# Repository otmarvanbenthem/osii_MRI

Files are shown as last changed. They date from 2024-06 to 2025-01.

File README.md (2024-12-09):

# OSII Mini 

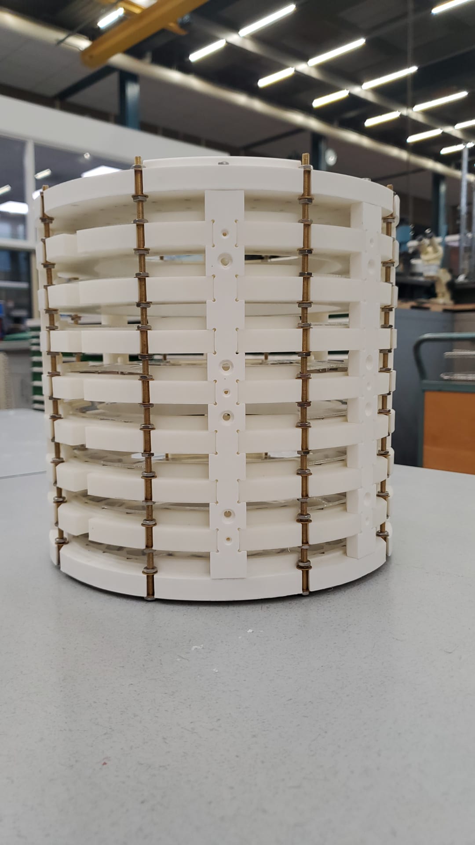
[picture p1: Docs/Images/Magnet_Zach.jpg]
Zach_magnet


Documentation for building the open source ultra low-field MRI for education

Magnetic Resonance Imaging (MRI) is one of the most powerful and versatile non-invasive medical imaging devices. 
Ultra low-field MRI scanners such as __OSII One__ have recently reached the maturity level of [attempting eligibility for standardization and medical certification](https://www.opensourceimaging.org/). 
These open source projects has pooled the knowledge and experience of many experts and can be built and maintained for a fraction of the price of current instruments. 

This educational project is a collaboration initiated by the [Lili's Proto Lab](https://www.uu.nl/lpl) with the aim of preparing a hands-on workshop for student teams to replicated an OSII-inspired functioning MRI.
Student teams can be a great force in progressing this field. 
Collectively, they can enhance the accuracy and utility of open-source MRI devices through rigorous calibration procedures, iterative testing, and collaboration with experts in both engineering and medical fields.  

## Getting started

These are the essential elements for creating a magnetic resonance image:
+ A uniform magenetic field B0
+ Coils for creating field gradients in x, y, and z -directions
+ Coils for sending and recieving pulses
+ Electronics for creating the imaging pulse sequences
+ Software to control the sequences and reconstructing the images

In this repository, we have split the steps into independent experiments so that one can start building each of the elements and persome some benchmark measurements.

## Building the main magnet
To create a uniform base field, we use the [Halbach Array](https://en.wikipedia.org/wiki/Halbach_array) construction. Check these [build instructions](./Docs/FrameAssembly) and [design files](./Build/HalbachFrame).

The current design is adopted from the OSII mini magnet designed by Dr. Joshua Harper from [Sustainable MRI Lab](smrilab.com) and Thomas O'Reilly and [Andrew Webb at Leiden University](https://www.universiteitleiden.nl/en/staffmembers/andrew-webb#tab-2). The main change in our design is using lids for keeping small magnets in place instead glueing them.  

__The Halbach Frame:__
	+ 120 mm inner diameter 
	+ DSV 100 x100 x100 mm
	+ 396 magnets 12x12x12 mm
	+ 50 mT
	+ around 1200 Euros for a completed magnet
	
### Verifying the field uniformity
To achieve MR imaging, the base magnetic field must be uniform. Based on experience, the maximum allowed field inhomgeneity is 3000 ppm. The field uniformity can be checked with a 3D scanner. [See instructions](./Docs/Fieldscanner) forconverting a 3D printer into such a scanner.

### Shimming the main magnet
The uncorrected fluctuations in Halbach with only big 6x6x6 mm magnets can be as high as 15000 ppm. This uniformity must be improved by adding extra magnets in a process called [shimming](./Docs/Shimming). 
Because of this process, each Halbach assembly is unique.

### Gradient coils
To create a three dimensional MRI, the spatial information must be [encoded in time, frequency and phase response](https://mriquestions.com/how-to-locate-signals.html#/) along these orthogonal axes. This encodig requires controlling applying various field gradients, dynamically. This encoding is done with 3 gradient coils. Check these [build instructions](./Build/GradientCoils).

### Send and recieve circuitry
MRI is based on measuring quantum effect called the spin echo. In short, the water molecules can be excited in a way that they emit a a measurable radio frequency signal at a specific delay after their excitation. The excitation pulse can be much stronger than the echo pulse, and therfore delicate circuitry is necessary to separate the spin echo from other possible spurious signals. Check these [design consideration](./Docs/RFCoils)

### The MRI console
In MRI literature, all the electronic boards that are used for generating and analyzing the required RF sequences are collectively called the MRI console. Once a uniform B0 is constructed and proper RF coils are embedded in the assembly frame, in principle the setup can be combined with suitable commercial or open source consoles. Here is a list of consoles that have been tested with various low-field MRI devices.

+ [Kea2](https://magritek.com/products/kea/) provided by magritek
+ [OCRA](https://openmri.github.io/ocra/) built on top of [STEMlab/Red Pitaya](https://www.redpitaya.com/f130/STEMlab-board)

## Latest news

The build instructions for the gluefree Halbach magnet are posted in the [Build](./Build/HalbachFrame) folder.

## Outcomes

Our main goal to support the student teams who collaborate in replicating this low field MRI. 
In parallel, all outputs of this collaboration will be shared with the sister MRI project such as the OSII ONE. 

## Team

+ Utrecht University, Lilis Proto Lab:
	+ Project lead: Sanli Faez
	+ Contributors: Zachary Meredith, Low Field Legends (Experiment Design class of 2024)

+ Universidad Paraguayo Alemana: 
	+ Project lead: Joshua Harper
	+ Contributors: 

+ NIST Boulder: 
	+ Project lead: Stephen Ogier
	+ Contributors: Katy Keenan

+ New York University, Interactive Telecommunications Program:
	+ Greg Shakar
	
## MRI Resources
More information about MRIs and their operations can be found below:
+ [MRI Questions website maintained by Allen D. Elster](https://mriquestions.com/index.html)
+ [OSI<sup>2</sup> Repository:](https://gitlab.com/osii) Here you can find additional information about the original OSI<sup>2</sup> ONE

### Related projects
Several groups worldwide have succeeded in replicating this device or have created similar designs. 

+ [OSI2 ONE MR Scanner](https://www.opensourceimaging.org/project/osii-one/)
+ [OCRA Console](https://openmri.github.io/ocra/)
+ [Earth-field NMR](https://phas.ubc.ca/~michal/Earthsfield/) 
+ [Hallbach Magnet designer](https://github.com/menkueclab/HalbachMRIDesigner)
+ [Table top MRI scanner](https://tabletop.martinos.org/index.php/Main_Page)
+ [Open Source relaxometry](https://github.com/mtwieg/NMR)

We would like to keep a curated list of open source low-field MRI projects. If you know of a project that has to be added to this list, send us a message or create a pull request.

For a long list of somewhat related open source hardware and software projects check [Open Source Imaging Initiative, OSI²](https://www.opensourceimaging.org/)

## Get involved

We don't accept pull request at this moment. Our goal is to open up for external contributions after November 2024 

This is a bottom-up initiative and participation in the project is on a voluntary basis. If you share the vision and goals of this initiative, we welcome all your compassionate support. 

You can support this initiative by any or all these options:
-	Recommending this workshop to enthusiastic students* in your institute.
-	Providing support, mentorship and expert advice to students who participate.
-	Hosting student teams in your lab/institute after the workshop for enhancing their builds.
-	Contributing to the preparation of the workshop with time, funding, or student assistants.
-	Financial support for purchasing the build materials.

Please contatct Sanli, @sanlifaez, for any inquiries.

## License

This project is licensed under [CERN Open Hardware Licence Version 2 - Weakly Reciprocal](./LICENSE).
Licenses of the individual modules of OSI² ONE that are used without alteration apply accordingly.

## (Funding)

This project has recieved an Open Science Hacker grant from the Lili's Proto Lab

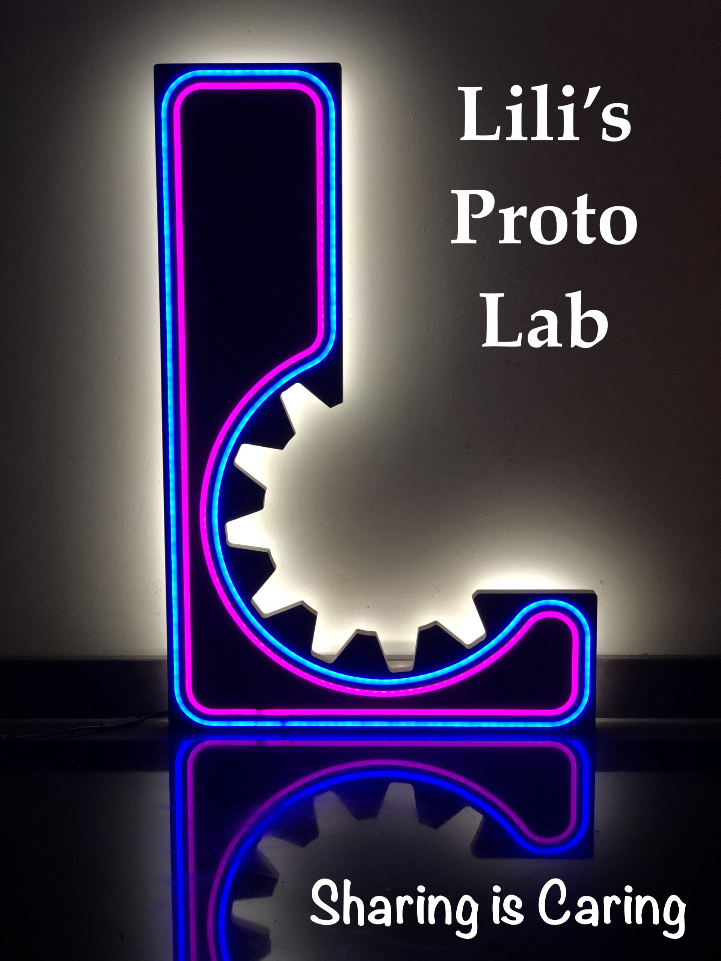
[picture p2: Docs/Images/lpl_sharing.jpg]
LPL sharing image


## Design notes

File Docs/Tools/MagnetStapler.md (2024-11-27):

# Magnet Stapler
The tools used to aid in reducing the finger pinching as the magnets are installed into the MRI frame rings.
I found that printing the tools with a resin printer yielded a better print quality. They can still be printed with an FDM printer though (using the same settings as the frame).

Tools to print:
  - [ ] [Stamp](../../Build/Tools/stamp-Body.step)
  - [ ] [Holder](../../Build/Tools/holder-Body.step)

| Stamp Model | Holder Model |
|:--:|:--:|
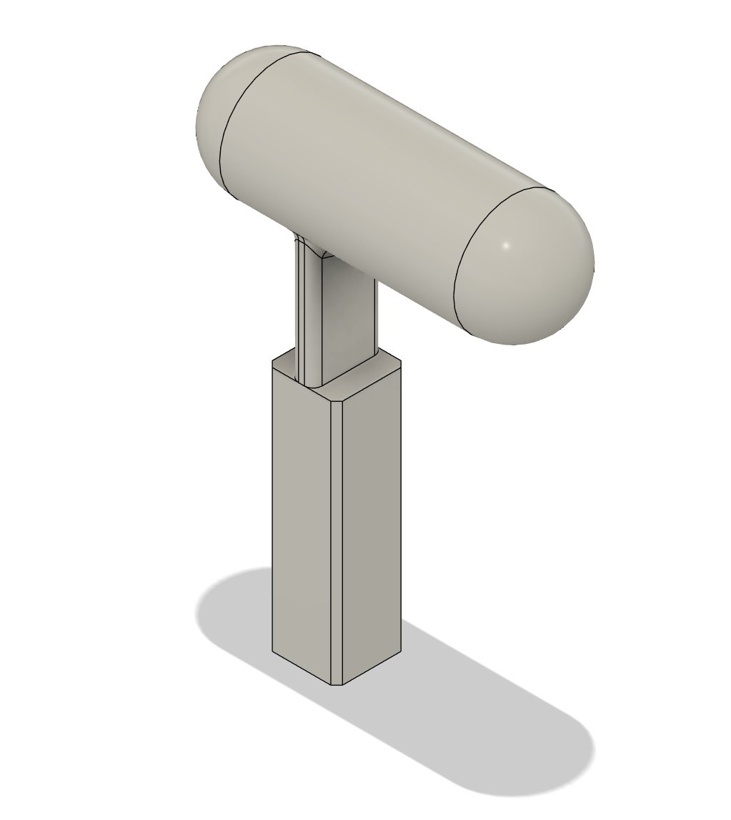
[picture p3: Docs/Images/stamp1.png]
printed ring example
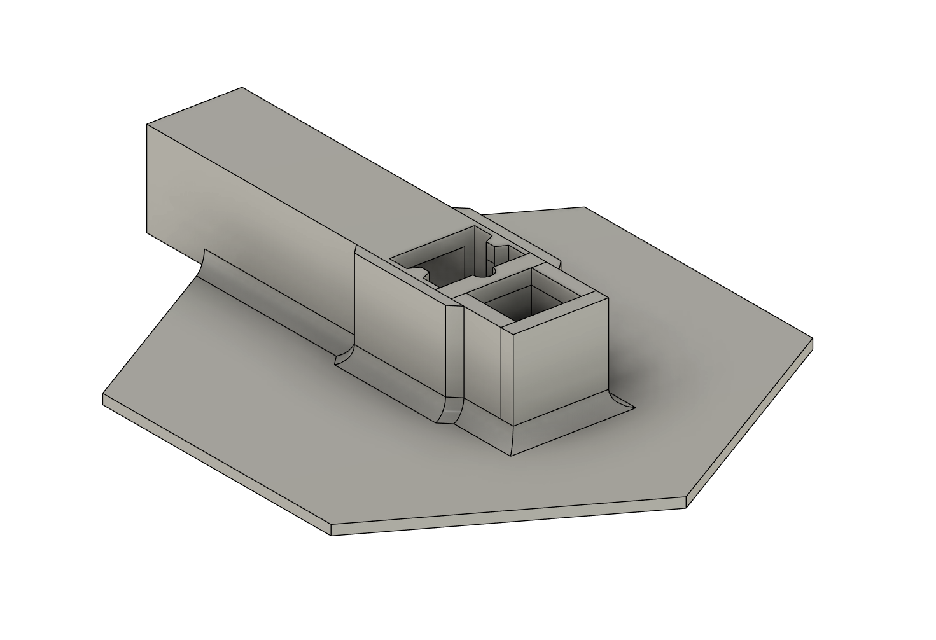
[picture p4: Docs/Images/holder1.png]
|||   

## Holder Modifications
I would also like to note that the current design of the holder was not ideal. The design was based off of usage for the origianl OSII ONE. With the addition of the clips designed to hold the plexi-glass on the ring, they constantly obstructed the stamp. A modification was made to raise the holder design in an attemp to counter this. This is also not a great solution, but it did end up holding for the duration of the mounting process.

The file for small modification can be found here:
  - [ ] [Fusion 360 file](../../Build/Tools/holder-modv2.f3d).
  - [ ] [DXF file](../../Build/Tools/holder_modv2.dxf).

| Stamp Mod Installed | Stamp Model |
|:--:|:--:|
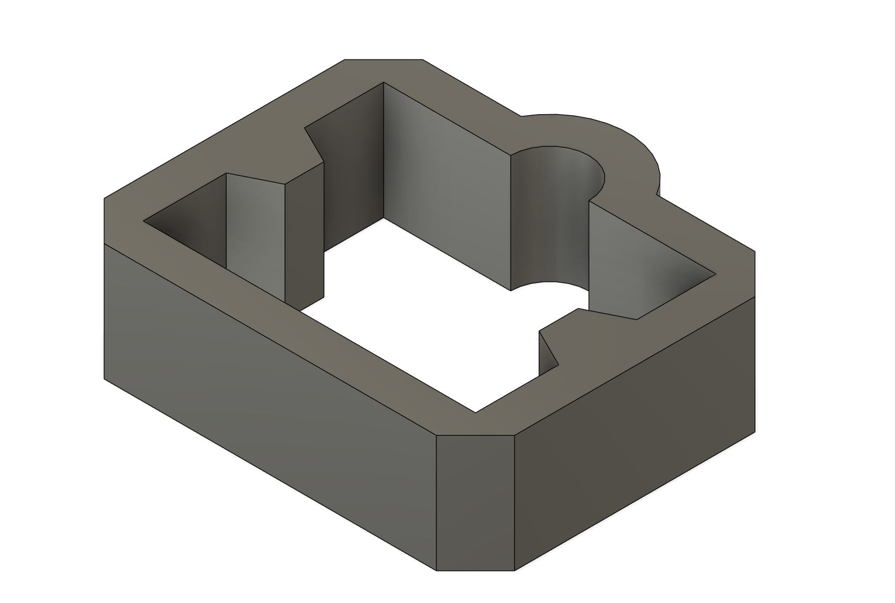
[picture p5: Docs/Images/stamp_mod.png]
|printed ring example||

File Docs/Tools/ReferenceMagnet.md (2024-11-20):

# Establishing the Reference Magnet

A reference magnet was used to check the magnetic field strength ($\vec{B}$- Field) and polarization of the Neodymium magnets used in the OSI<sup>2</sup> MINI build.

## Required Hardware
- [ ] 1 Arduino Uno (or similar Arduino product)
- [ ] 1 USB cable (to connect the Arduino to the computer)
- [ ] 3 jumper cables (to connect the Hall Effect Sensor to the Arduino)
- [ ] 1 Computer
- [ ] 1 [Hall Effect Sensor](../BackCatalog/A1302K-67Y_hall_sensor.pdf)
- [ ] 1 [*Magnet Test Station*](../../Build/Tools/Frame-TestMagnetSupport.step)
- [ ] 1 Spacer ([*Spacer_A0*](../../Build/Tools/Spacer_A0-Spacer.step) or [*Spacer_A1*](../../Build/Tools/Spacer_A1-Spacer.step))
- [ ] 1 Neodymium Magnet (this becomes your reference)

## Required Software
- [ ] Python 3 with libraries:
  + PyQt6
  + numpy
  + pyserial

## To Obtain a Reference Magnet
  1. Select one of the magnets from the batch.
  2. Inspect magnet to ensure there are no damages to the magnet.

  | Damaged Magnet 1 | Damaged Magnet 2 |
  | :---: | :---: |
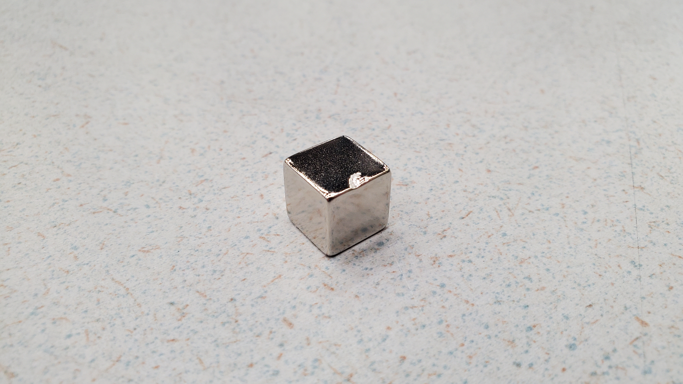
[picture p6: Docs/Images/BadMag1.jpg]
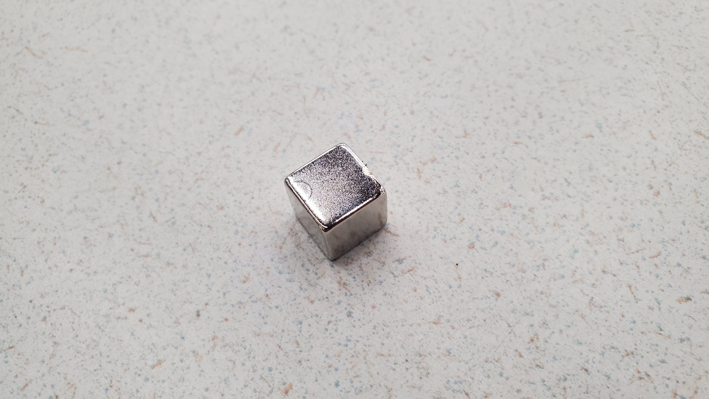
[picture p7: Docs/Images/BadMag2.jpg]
   | 

  3. Insert the magnet and Hall Effect sensor into the [*Magnet Test Station*](../../Build/Tools/Frame-TestMagnetSupport.step).

  | Magnet and Sensor in test station | Sensor Wiring |
  | :---: | :--: |
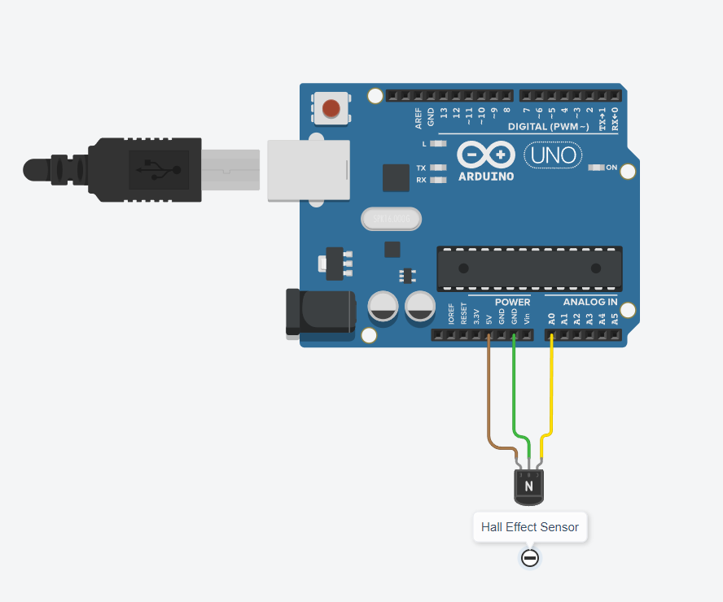
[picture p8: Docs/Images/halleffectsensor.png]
Sensor Wiring
  |Magnet and sensor in test station||
  
  5. Download the [*Arduino Script*](../../Software/MagnetTestStation) to interface with the Arduino.
      - Connect the Arduino to your USB port.
      - Ensure your wiring matches the above schematic.
      - Update the analog pin name to which the Hall sensor is connected to inside the Arduino sketch code.
          ```cpp
            short pins[] = {A0};
          ```
      - Upload the Arduino sketch to the Arduino.

  7. Keep the Arduino connectedd to your computer and make sure you have downloaded the [*Python Scripts*](../../Software/MagnetTestStation).
      - Run the Python script `mainInterface.py` to trigger the UI.
      - In the $${\color{lightgreen}Options}$$ section, properly fill out the number of Hall sensors, sensitivity, serial port the Arduino is connected, and file location/name.
      - Press $${\color{orange}Connect}$$ to establish communication with the Arduino.
      - Press $${\color{orange}Start \space Measurements}$$ to start a live measurement of the magnetic field.
      - Press $${\color{orange}Store}$$ to log individual points into a log file.
      - Press $${\color{orange}Zero}$$ to set a zero point during measurement.
        
  | mainInterface.py | log file |
  | :---: | :---: |
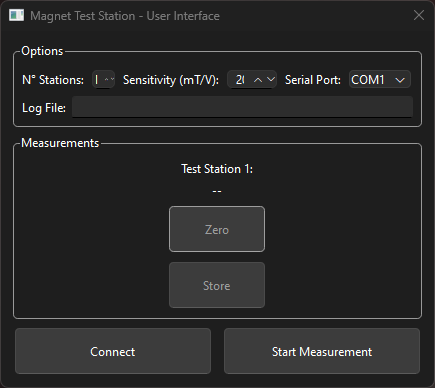
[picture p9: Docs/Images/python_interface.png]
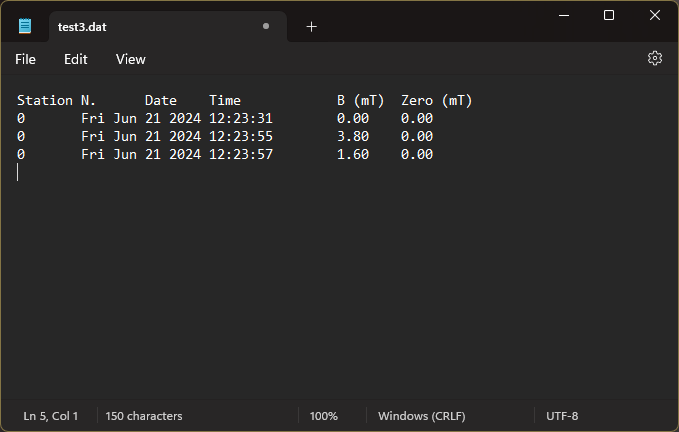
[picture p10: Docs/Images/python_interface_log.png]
   | 

## Understanding the Hall Effect
> [!NOTE]
> Whether the north or south pole of the magnet is facing the Hall Effect sensor is irrelevant. The important part is ensuring that which ever pole you choose, you are consistent throughout the project.

For now, let's assume we want the south pole of the magnet to be marked.

Once the Arduino is properly connected and the Magnet Testing Script recognizes the Hall Effect sensor, understanding what the readout of the sensor represents is important. The orientation of the Hall Effect sensor, as well as the magnet, affect the readout. With the front of the senor facing the magnet, the readout should be *NEGATIVE* if the South Pole of the magnet is facing the sensor. Moving the magnet closer to the sensor causes a voltage drop, while a voltage increase occurs when the magnet is moved away from the sensor. 

| Lower Voltage | Higher Voltage |
| :---: | :--: |
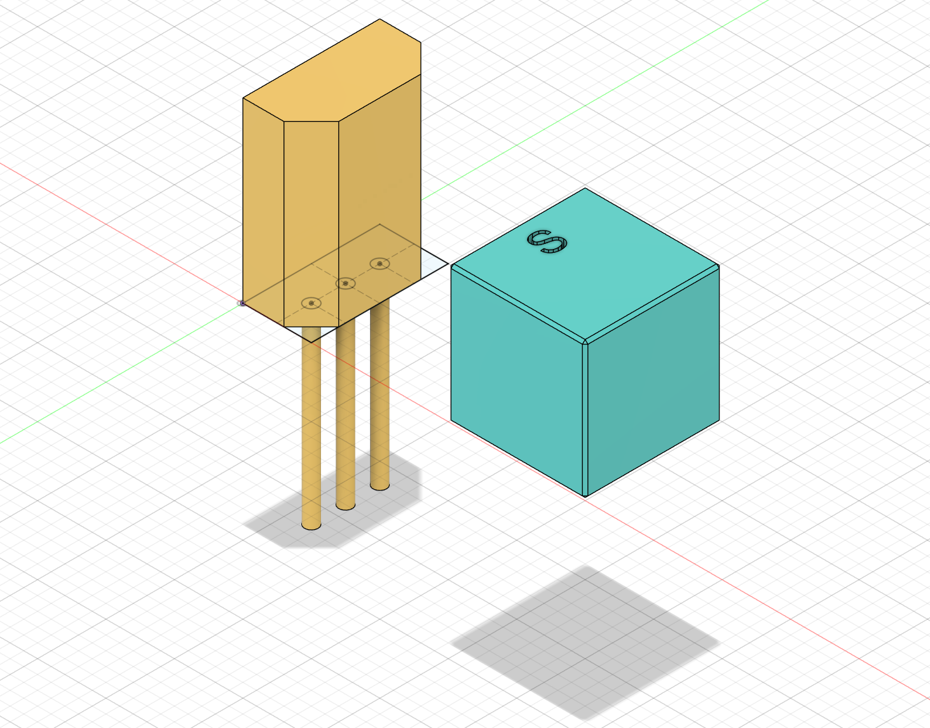
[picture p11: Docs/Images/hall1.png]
lower voltage
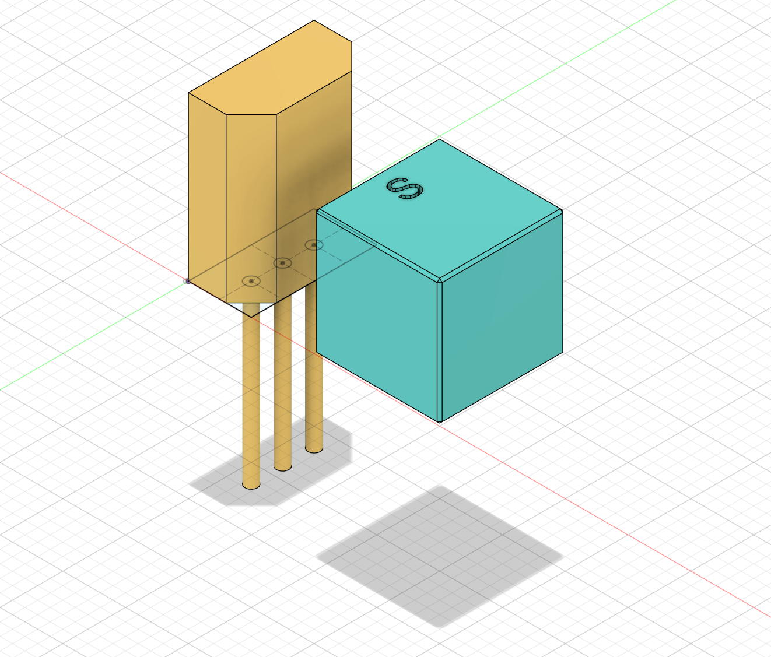
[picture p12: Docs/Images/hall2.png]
higher voltage
|| 

The purpose of the magnet test station is then to force the magnet to be at a consistent distance from the sensor. This will come in handy later on when we test the rest of the magnets for their $\vec{B}$- Field. A magnet can then easily be identified if its $\vec{B}$- Field is out of specification.

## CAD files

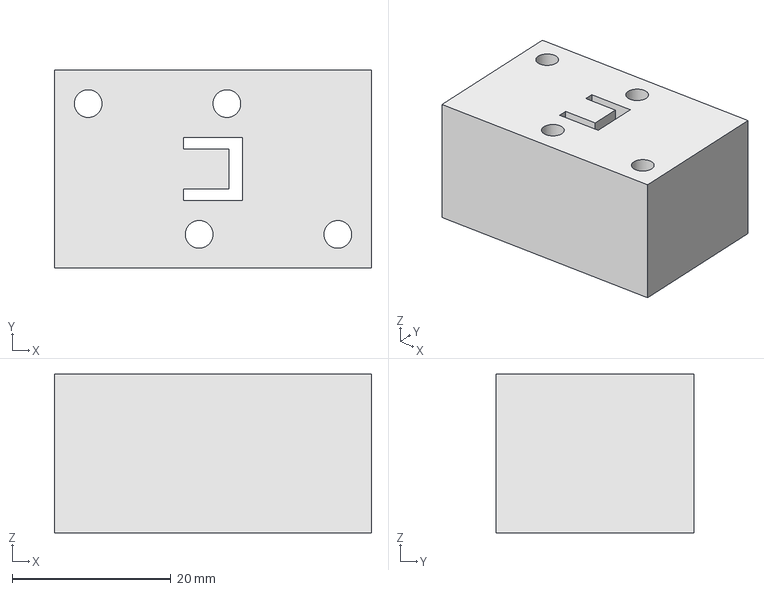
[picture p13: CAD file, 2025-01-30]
Build/FieldScanner/Code/robotic arm/3D-attachment.FCStd
40.0 x 25.0 x 20.0 mm

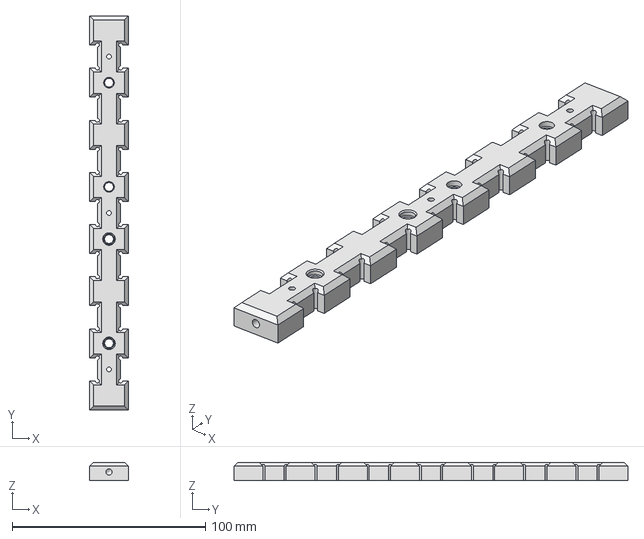
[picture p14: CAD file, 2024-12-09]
Build/HalbachFrame/Locating_Bar/Locating_bar v1.step
20.0 x 204.0 x 9.50 mm

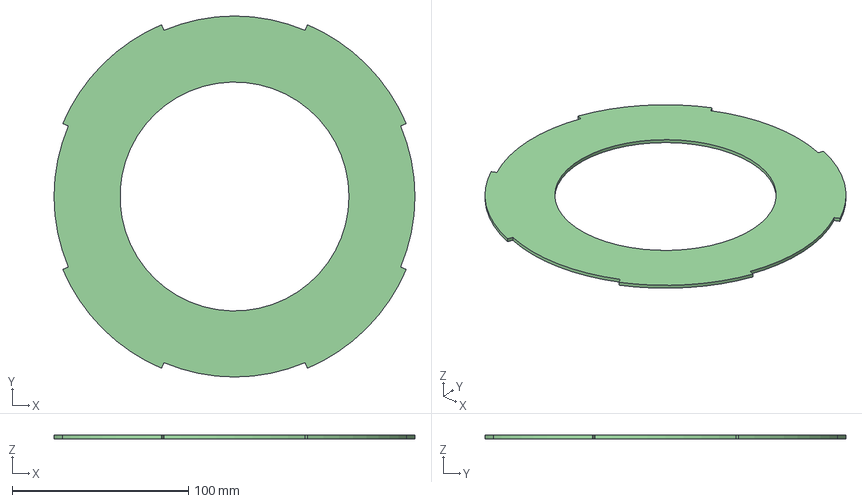
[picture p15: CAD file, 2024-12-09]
Build/HalbachFrame/Magnet_Lid/STEP/Lid_B_V2 v3.step
205.0 x 205.0 x 2.00 mm

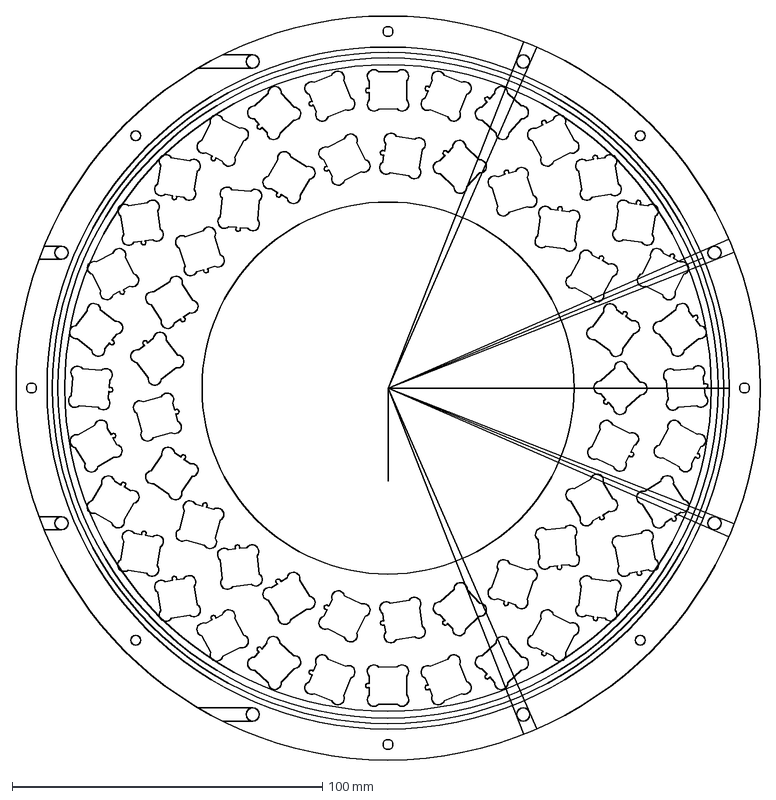
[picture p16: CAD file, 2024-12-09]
Build/HalbachFrame/Rings/DXF_Files/Ring_4_V3 v10.dxf
240.0 x 240.0 mm

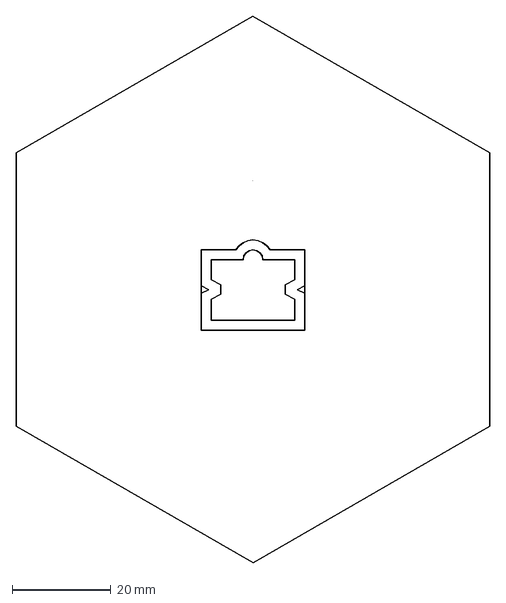
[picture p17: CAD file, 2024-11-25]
Build/Tools/holder_modv2.dxf
96.0 x 110.9 mm

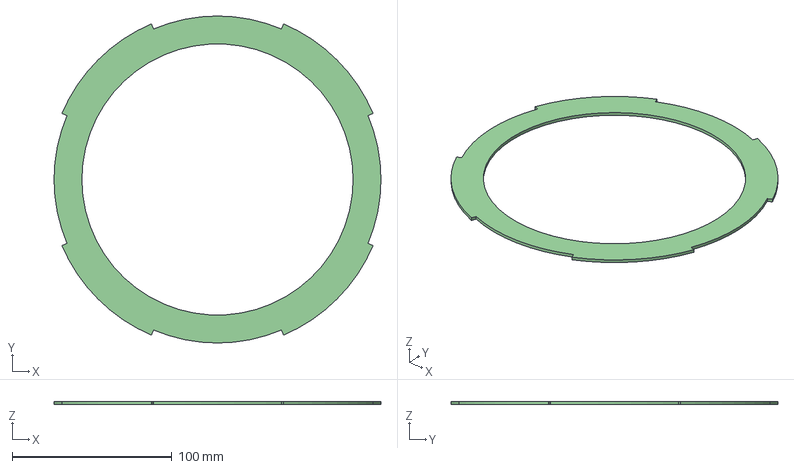
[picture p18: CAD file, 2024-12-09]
Build/HalbachFrame/Magnet_Lid/STEP/Lid_A_V2 v2.step
205.0 x 205.0 x 2.00 mm

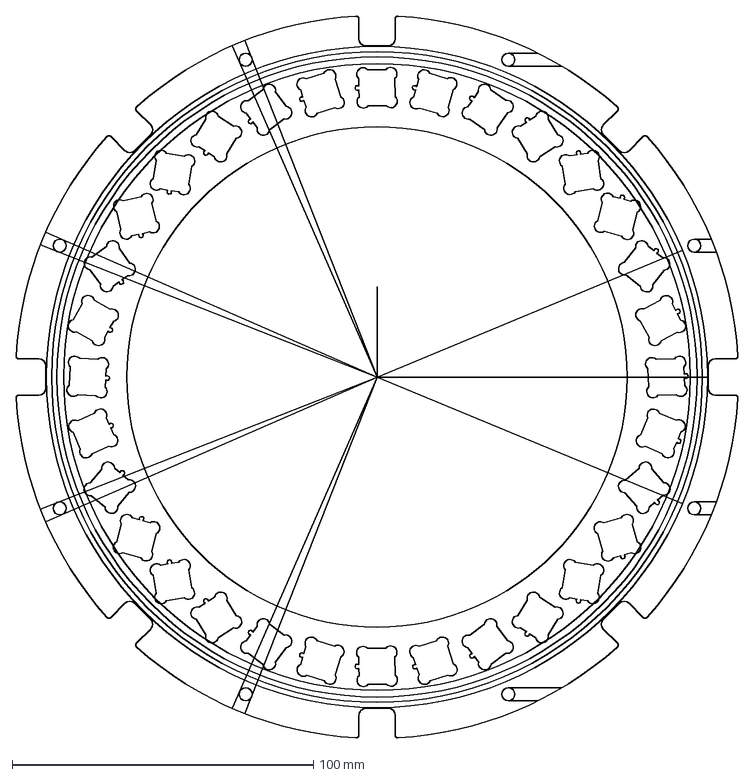
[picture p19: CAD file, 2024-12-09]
Build/HalbachFrame/Rings/DXF_Files/Ring_3_V3_180 v2.dxf
239.6 x 239.6 mm

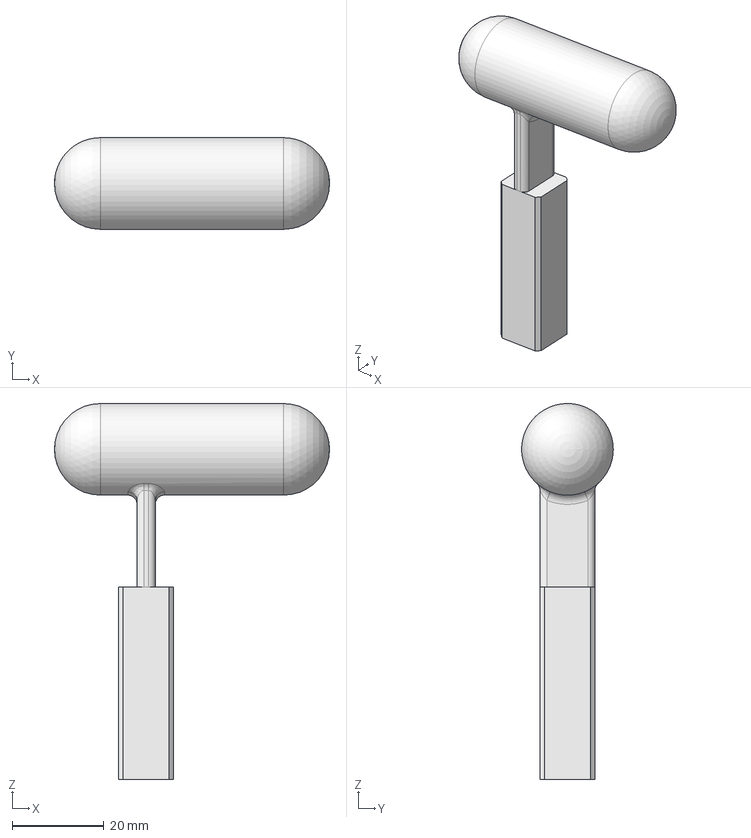
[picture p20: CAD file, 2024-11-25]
Build/Tools/stamp-Body.step
60.0 x 20.0 x 82.0 mm

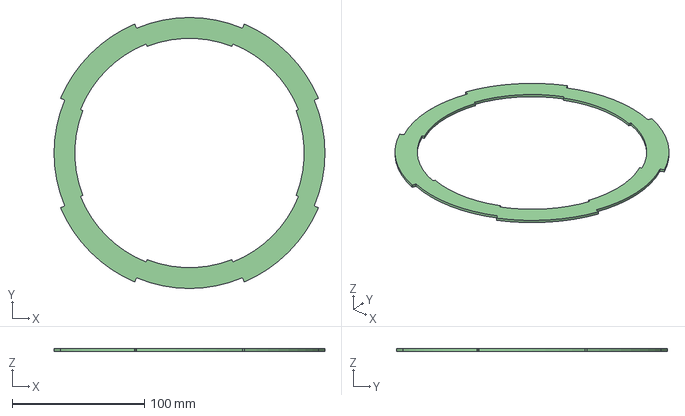
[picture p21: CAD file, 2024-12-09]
Build/HalbachFrame/Magnet_Lid/STEP/Lid_A_V2_xtraclip v3.step
205.0 x 205.0 x 2.00 mm

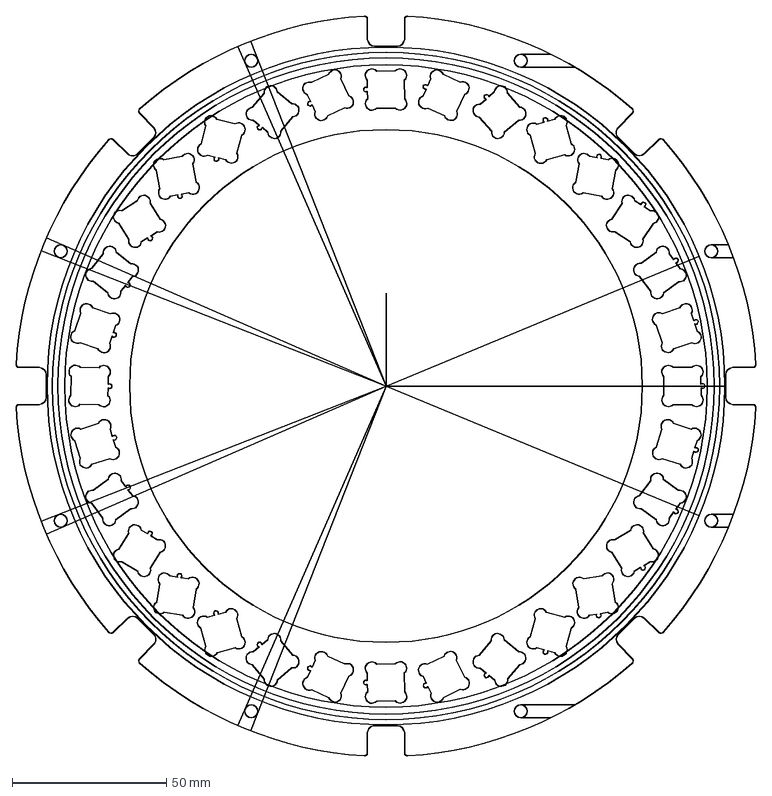
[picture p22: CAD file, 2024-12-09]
Build/HalbachFrame/Rings/DXF_Files/Ring_2_V3_180 v2.dxf
239.6 x 239.6 mm

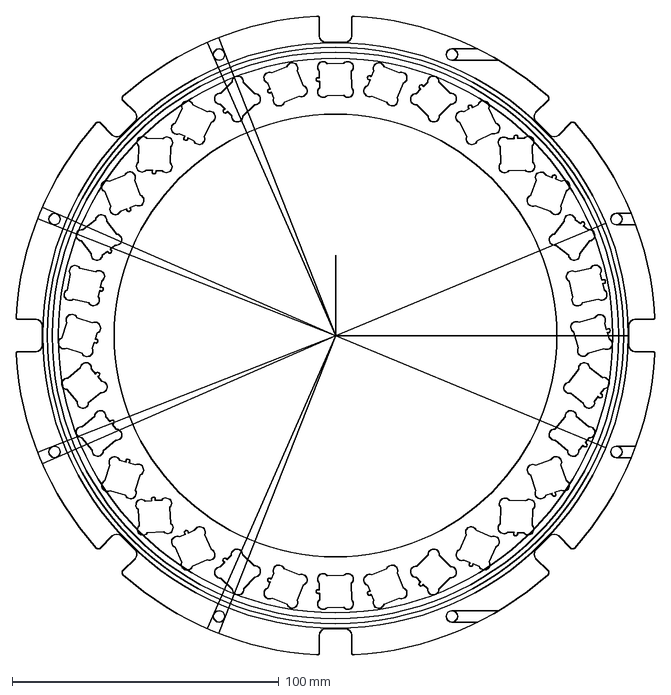
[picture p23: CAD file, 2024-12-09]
Build/HalbachFrame/Rings/DXF_Files/Ring_1_V3_180 v5.dxf
239.6 x 239.6 mm

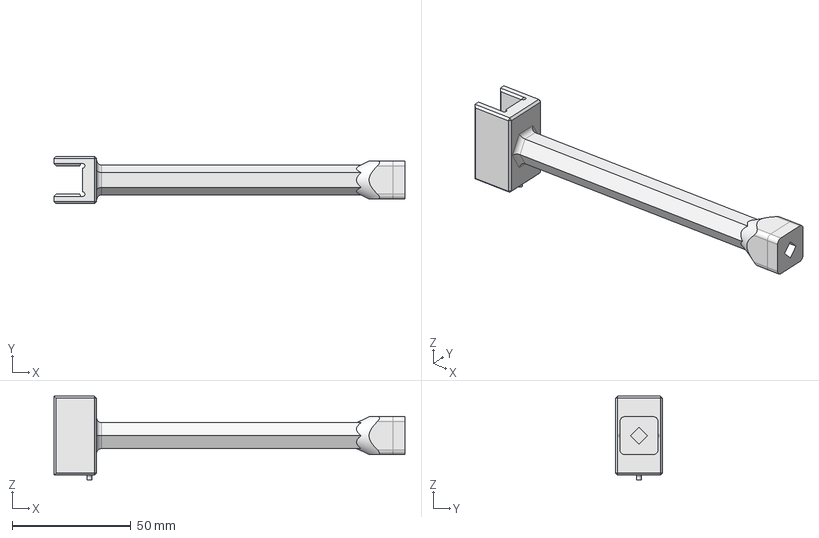
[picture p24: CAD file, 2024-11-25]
Build/Tools/wrench.FCStd
148.0 x 20.0 x 35.3 mm

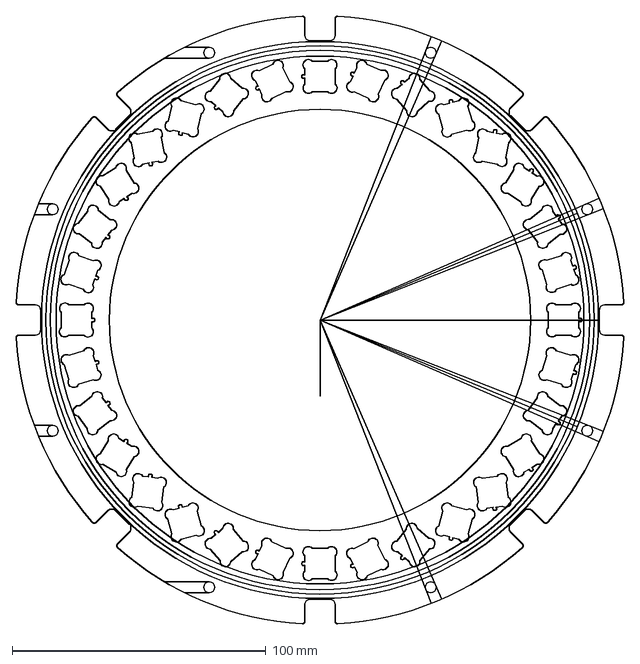
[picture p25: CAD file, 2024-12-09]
Build/HalbachFrame/Rings/DXF_Files/Ring_2_V3 v4.dxf
239.6 x 239.6 mm

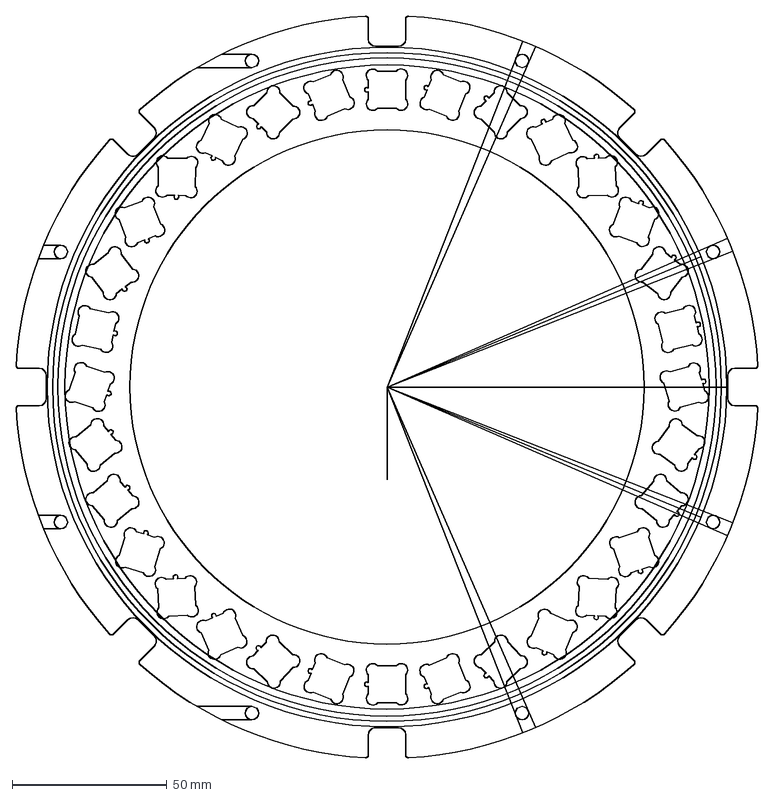
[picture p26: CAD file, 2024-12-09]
Build/HalbachFrame/Rings/DXF_Files/Ring_1_V3 v1.dxf
239.6 x 239.6 mm

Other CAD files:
Build/HalbachFrame/Hardware/M4_threaded_brass v1.dxf
Build/Tools/stamp.FCStd
Build/Tools/wrench-Body.step
Build/HalbachFrame/Hardware/93187A150_NO THREADS_Brass Thin Hex Nut v1.dxf
Build/HalbachFrame/Hardware/93187A150_NO THREADS_Brass Thin Hex Nut v1.f3d
Build/HalbachFrame/Hardware/94500A283_NO THREADS_316 Stainless Steel Button Head Hex Drive Screws v1.dxf
Build/HalbachFrame/Hardware/94500A283_NO THREADS_316 Stainless Steel Button Head Hex Drive Screws v1.f3d
Build/HalbachFrame/Hardware/98691A114_General Purpose Brass Washer v1.dxf
Build/HalbachFrame/Hardware/98691A114_General Purpose Brass Washer v1.f3d
Build/HalbachFrame/Hardware/M4_threaded_brass v1.f3d
Build/HalbachFrame/Locating_Bar/Locating_bar v1.dxf
Build/HalbachFrame/Locating_Bar/Locating_bar v1.f3d
Build/HalbachFrame/Magnet_Lid/DXF_Files/Lid_A_V2 v2.dxf
Build/HalbachFrame/Magnet_Lid/DXF_Files/Lid_A_V2_xtraclip v3.dxf
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

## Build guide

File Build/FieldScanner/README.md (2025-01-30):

## Name
3-D magnetic field scanner directory guide.

## Description
In this README, we outline the structure of this projects directory.

## Content
The directory is divided into four sub directories: Code, Projects_Files. I will now explain these directories.

-Code: Here we will save all codes used for this project, which will be divided into codes for the sensor and for the 3-D printer, also a code has been provided to read in the data from the sensor codes.

-Project_Files: Here we will keep files relevant to evaluation regarding the project. This includes, but is not limited to: figures, results, documentation etc.

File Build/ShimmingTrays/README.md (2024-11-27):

# Magnets

We are replicating the OSII mini magnet designed by Dr. Joshua Harper from [Sustainable MRI Lab](smrilab.com) which is based on the original work of Thomas O'Reilly and Andrew Webb at Leiden University.

+ __The Halbach magnet:__
	+ 120 mm inner diameter 
	+ DSV 100 x100 x100 mm
	+ 396 magnets 12x12x12 mm
	+ 50 mT
	+ around 1500 Euros for a completed magnet

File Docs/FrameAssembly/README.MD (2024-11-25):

# Assembing the 3D-Printed Frame and Halbach Magnets

## Description
This directory contains:
1. [Printing the rings](./PrintFrame.md)
2. [Installing the magnets](./MagnetAssembly.md) that generate the main static field
3. [Mounting the rings](./FrameAssembly.md)

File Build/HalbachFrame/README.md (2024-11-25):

# Basic Frame Information

> [!NOTE]
> If you want to access any of the Fusion 360 files supplied, you can either go into a sub-folder and select specific models to load, or in this current directory you can load the most up to date $${\color{orange}OSII \space MINI}$$ version.

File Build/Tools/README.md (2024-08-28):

# **The Right Tools for the Job**

This folder gives informative descriptions and CAD models to the custom tools used in this project. These tools are 3D printed prior to beginning construction.

## Printer settings and consumables
Printers Used: 
  - Prusa MK3.9 (Heatbed = Steel)
  - Prusa XL (Heatbed = Satin Powder-Coated)
    
Filament & Filament Settings:
  - 3D Jake eco PLA Tough: Transparent
  - Extruder Temp: 205 C
  - Bed Temp: 60 C
  - Nozzle Diameter: 0.40 mm
  - Layer Height: 0.20 mm (speed)

> [!NOTE]
> All printer settings are set in perspective to PrusaSlicer

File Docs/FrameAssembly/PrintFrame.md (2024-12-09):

# Printing the Frame

## Printer settings and consumables
Printers Used: 
  - Prusa MK3.9 (Heatbed = Steel)
  - Prusa XL (Heatbed = Satin Powder-Coated)
    
Filament & Filament Settings:
  - 3D Jake eco PLA Tough: Transparent
  - Extruder Temp: 205 C
  - Bed Temp: 60 C
  - Nozzle Diameter: 0.40 mm
  - Layer Height: 0.20 mm (speed)

> [!NOTE]
> All printer settings are set in perspective to PrusaSlicer

## About the Rings
| Ring Example | Version Labelling |
| :---: | :---: |
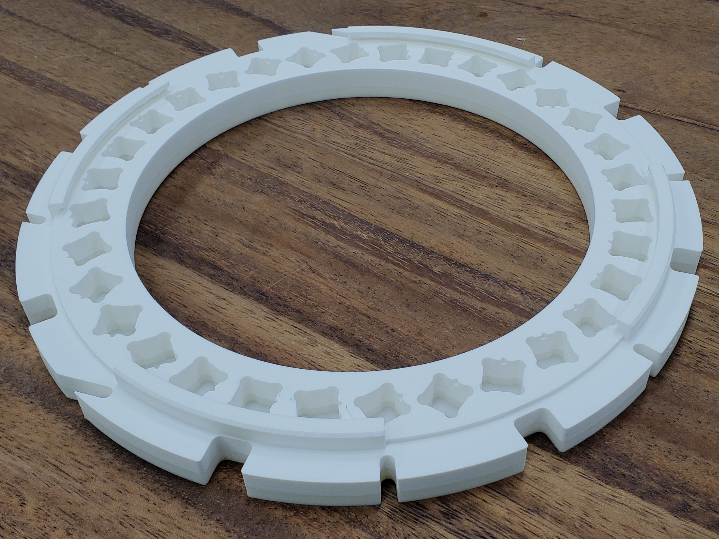
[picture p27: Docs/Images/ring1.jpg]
printed ring example
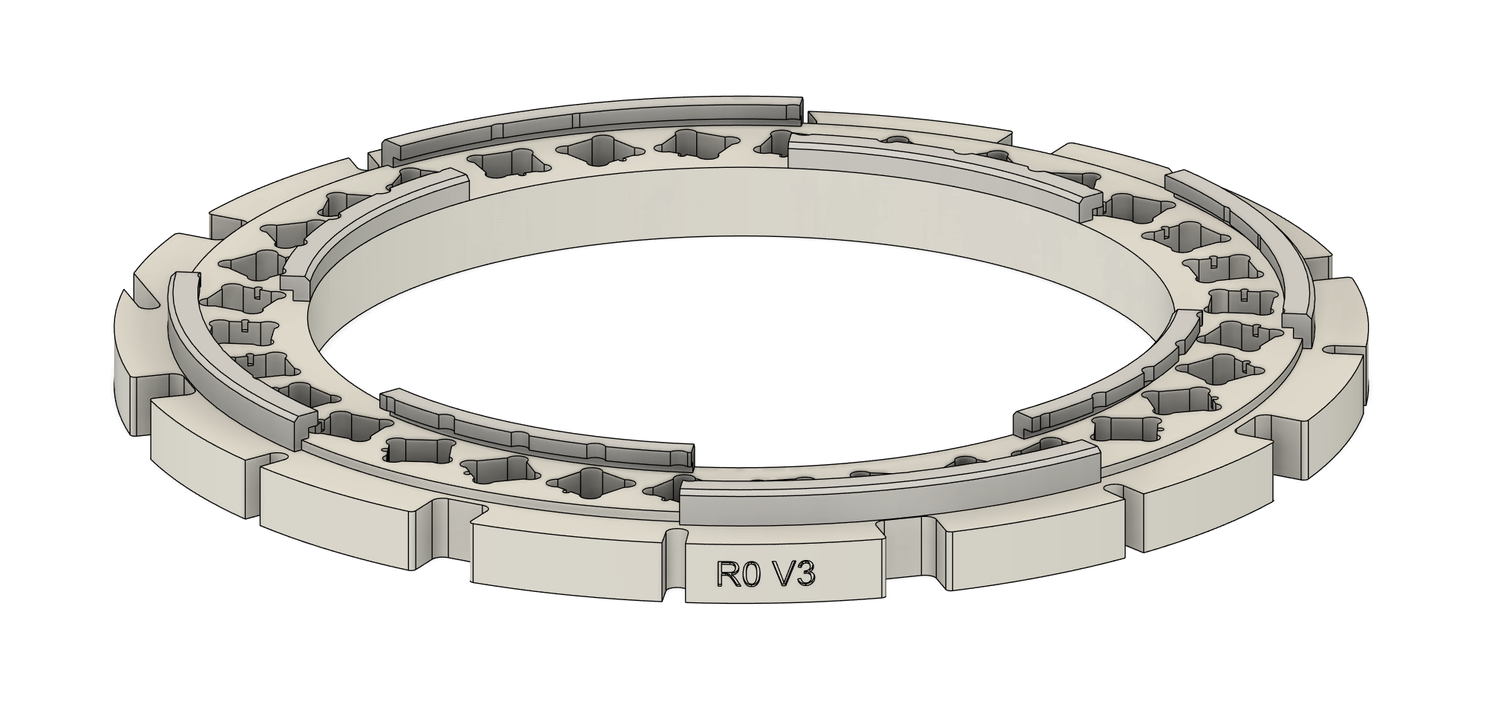
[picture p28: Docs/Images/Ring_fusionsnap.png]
CAD drawing of ring
|||

There are 9 rings to print in total. Each ring is physically labeled depending on location and orientation. Below I will elaborate on how the ring itself is labeled, what it refers to, and the filename it correlates to. It is good to note that the lower case version numbers $${\color{orange}v3 \space versus \space V3}$$ are artifacts from the versioning within Fusion 360. It is wise to simply use the latest Fusion version when possible.

For example: 
  - [ ] R4 V3 = Ring 4 version 3 = Ring_4_V3 v10.f3z
  - [ ] R4R V3 = Ring 4 Rotated version 3 = Ring_4_V3_180 v3.f3z

For each ring, the Fusion 360 files and the DXF files can be found [here](../Build/HalbachFrame/Rings).

## About the Locating Bar
| Locating Bar | 3D Model |
| :---: | :---: |
|locating bar image|CAD drawing of locating bar|

There are 8 locating bars that need to be printed for this design. Versions of this file can be found [here](../Build/HalbachFrame/Locating_Bar).

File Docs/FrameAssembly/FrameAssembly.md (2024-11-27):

# Frame Assembly

Once the magnets are mounted securely into each ring, and the plexi-glass is twist locked into place, the rings are ready to be assembled into a single assembly.
This part can be a bit tricky with the current design and future iterations will need modifications to streamline this process.

> [!NOTE]
> Rings 4 and 4R have different dimensions than the rest of the rings and will be assembled last, acting like end caps to the structure.

### Step 1: 
Start with rings R3 and R2. Taking only one of the locating bars, insert the two rings into their apropriate slots. Keep in mind the orientation of each ring is the same and the version labels should all face the same direction.

| Mounting R3 | Mounting R2 |
|:--:|:--:|
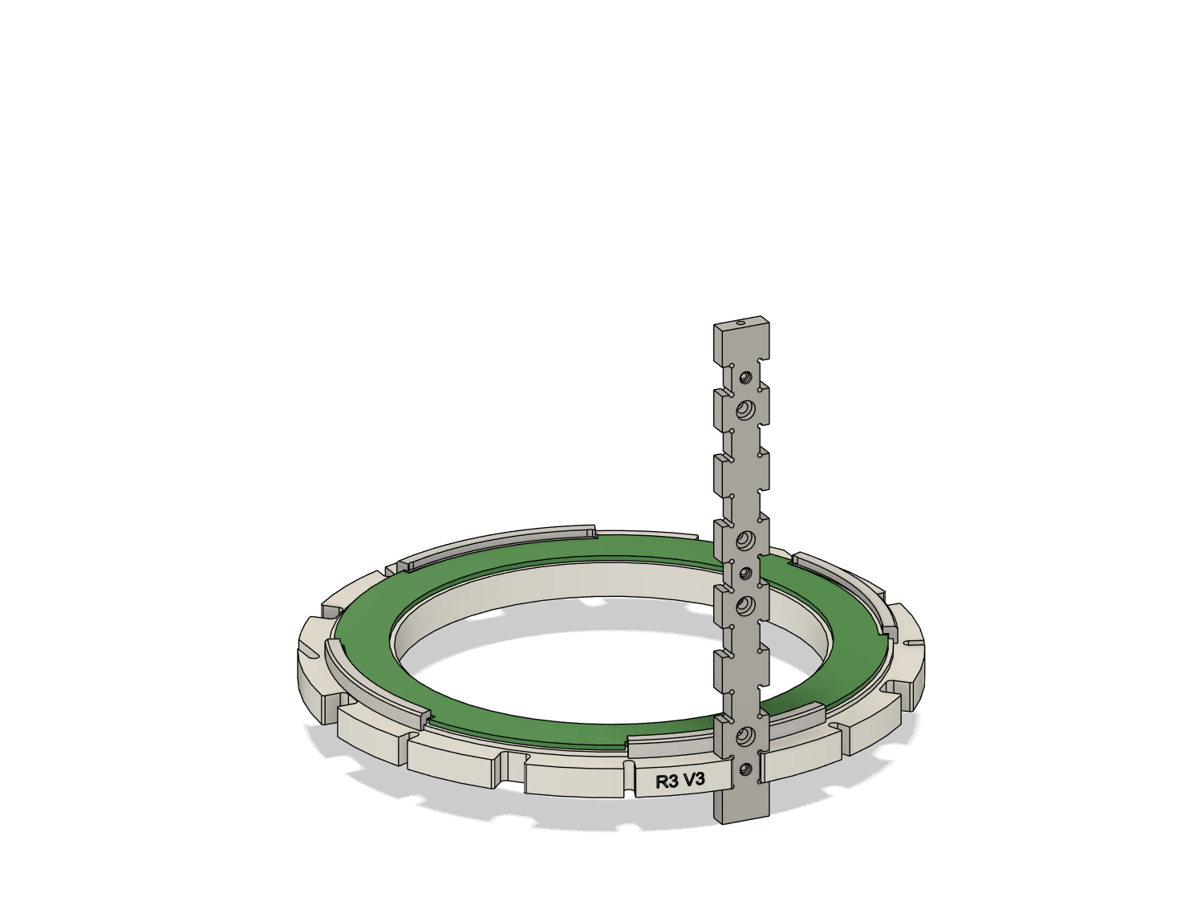
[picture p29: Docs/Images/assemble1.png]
image inserting R3 into locating bar
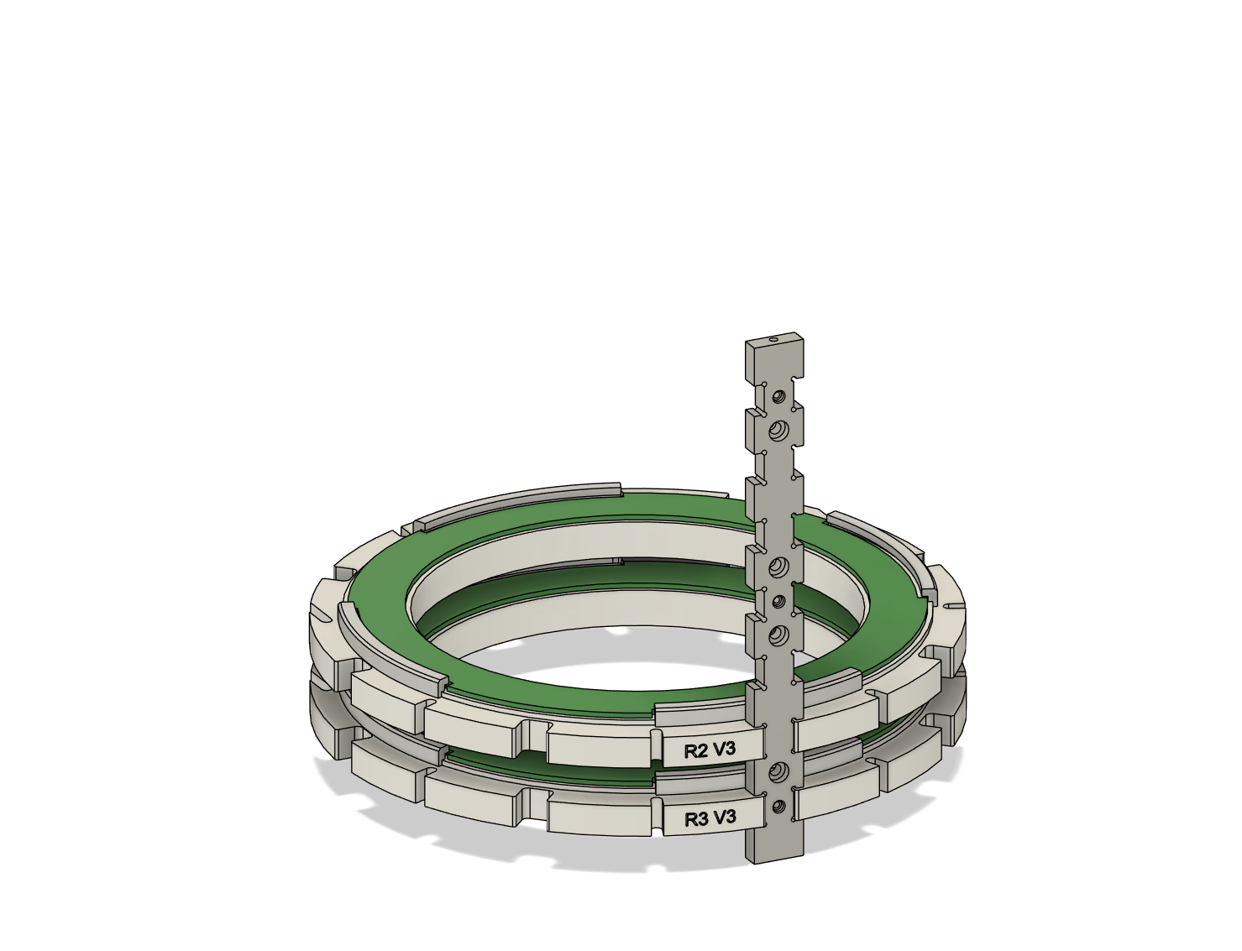
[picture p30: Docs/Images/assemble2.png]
image inserting R2 into locating bar
|||

### Step 2: 
Insert rings R1 and R0.

| Mounting R1 | Mounting R0 |
|:--:|:--:|
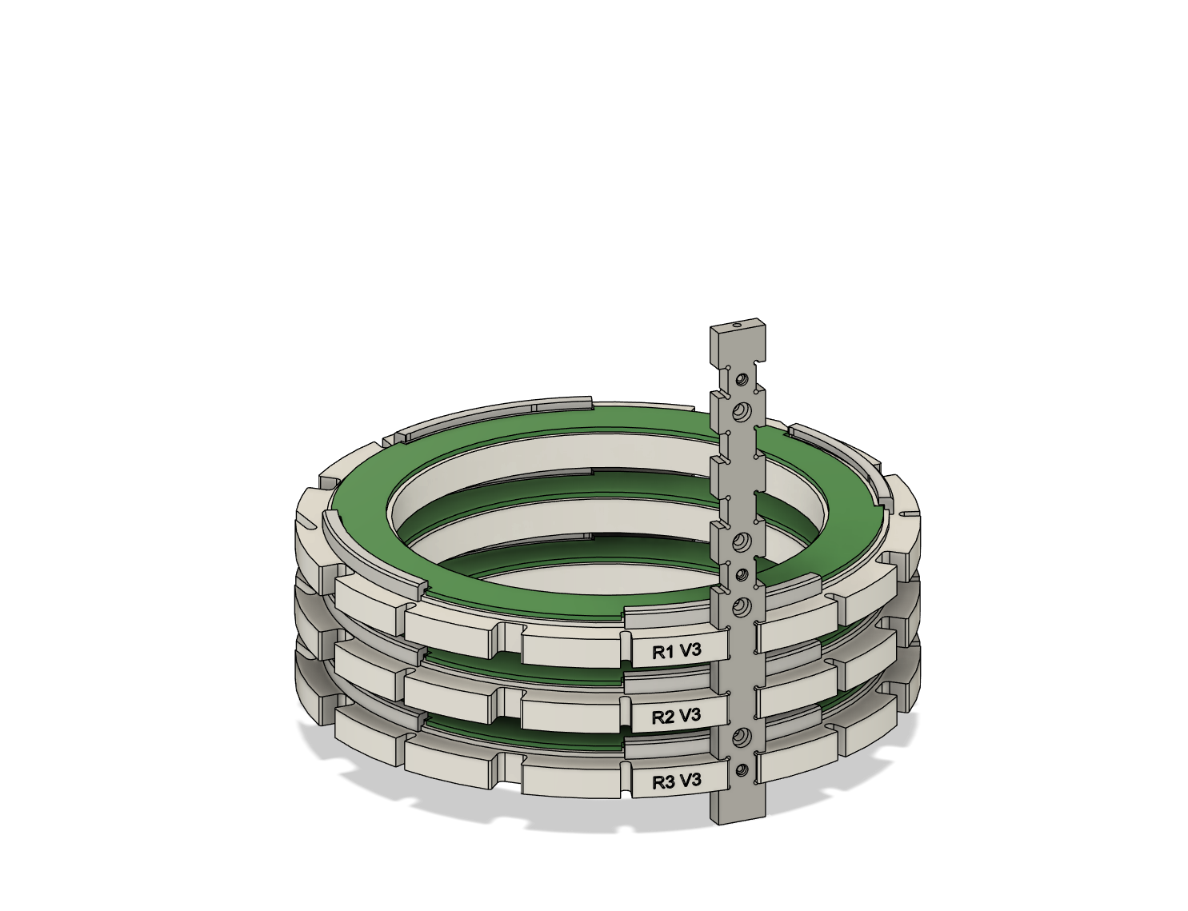
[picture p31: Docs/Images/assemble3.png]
image inserting R1 into locating bar
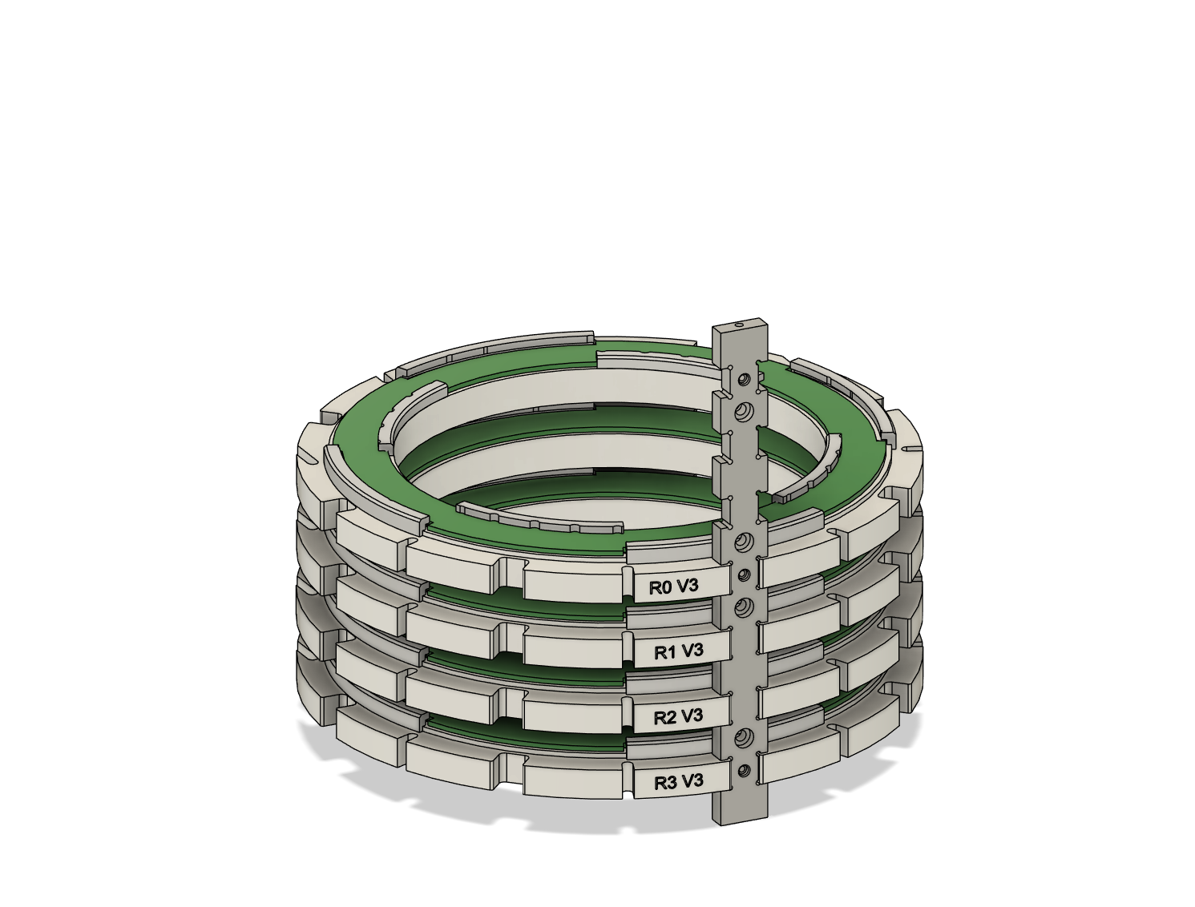
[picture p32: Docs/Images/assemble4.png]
image inserting R0 into locating bar
|||

### Step 3: 
Insert rings R1R and R2R.

| Mounting R1R | Mounting R2R |
|:--:|:--:|
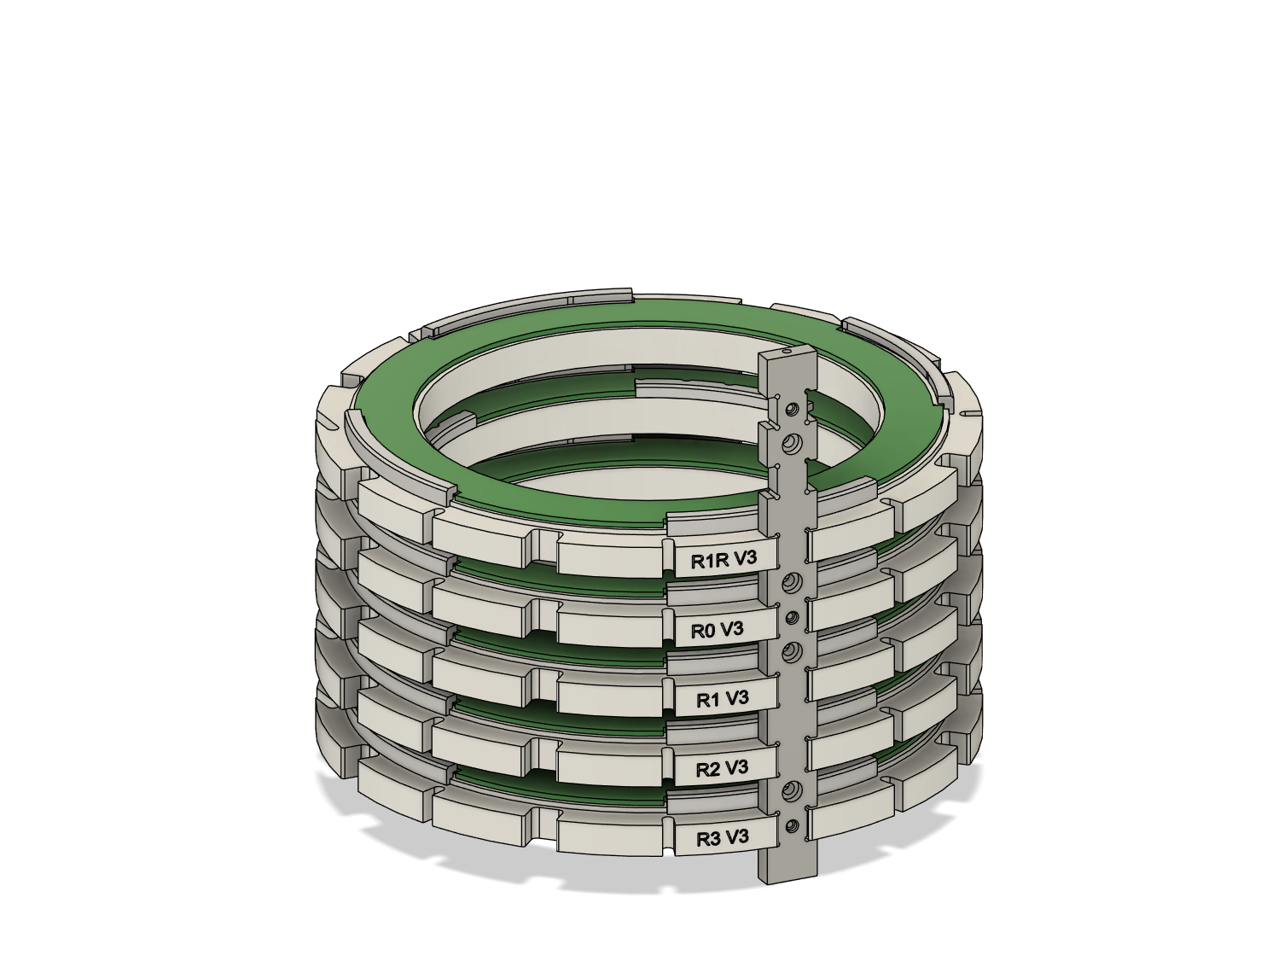
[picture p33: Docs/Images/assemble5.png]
image inserting R1R into locating bar
||image inserting R2R into locating bar|

### Step 3: 
Insert ring R3R

| Mounting R3R | 
|:--:|
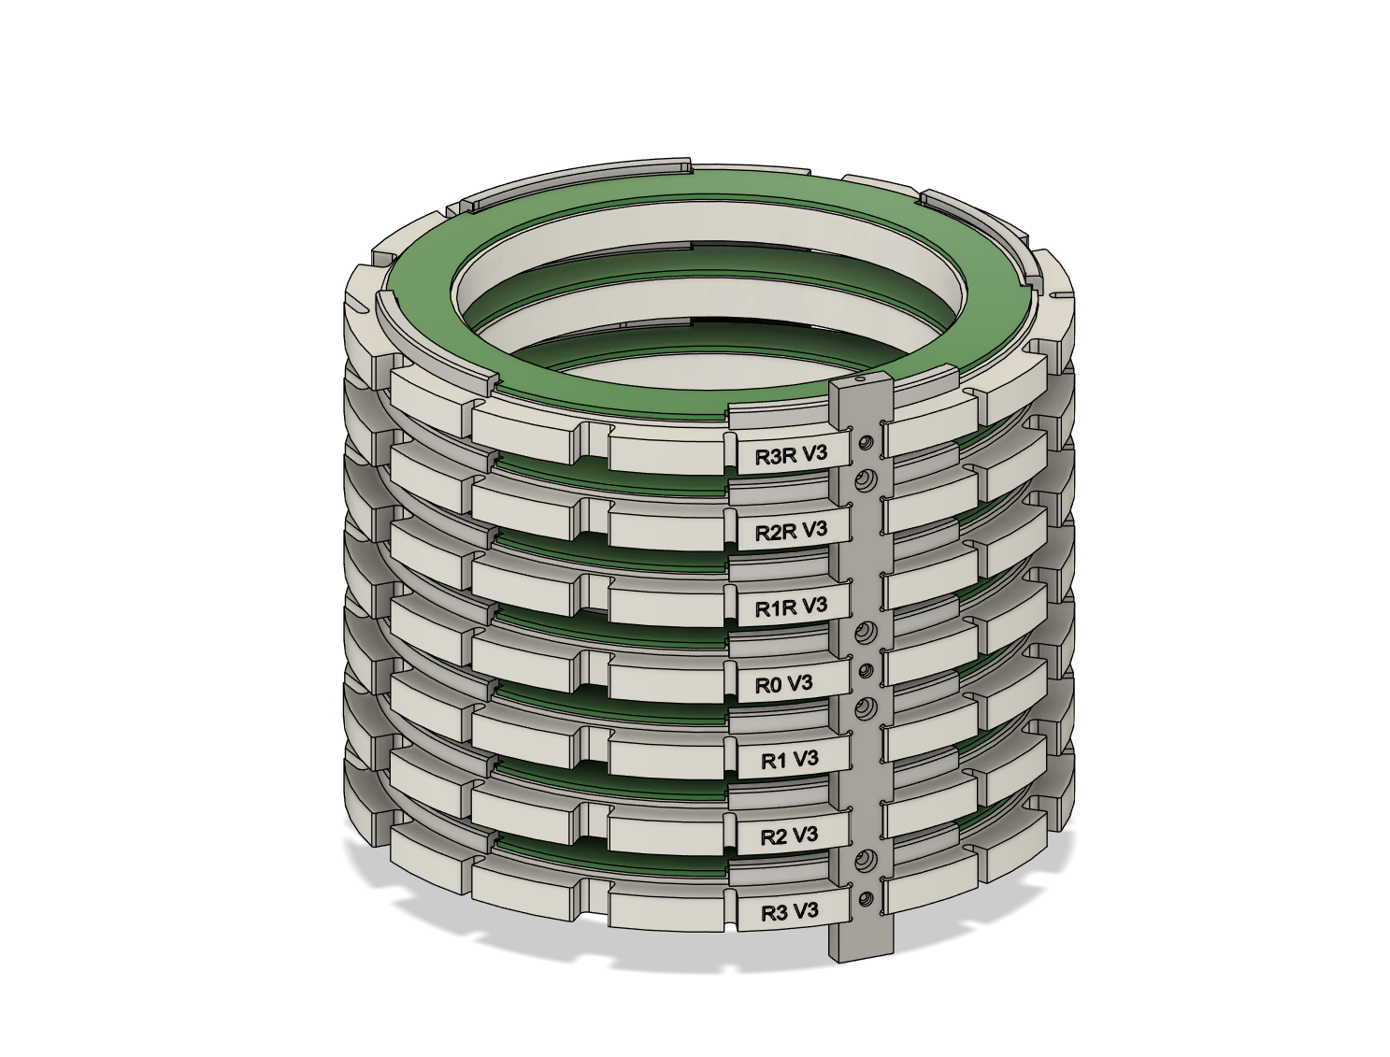
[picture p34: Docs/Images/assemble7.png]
image inserting R1R into locating bar
||

### Step 3: 
Attach rings R4 and R4R, attach the rest of the locating bars and R4 and R4R into the locating bars.

| Mounting R4 and R4R | Mounting Locating Bars |
|:--:|:--:|
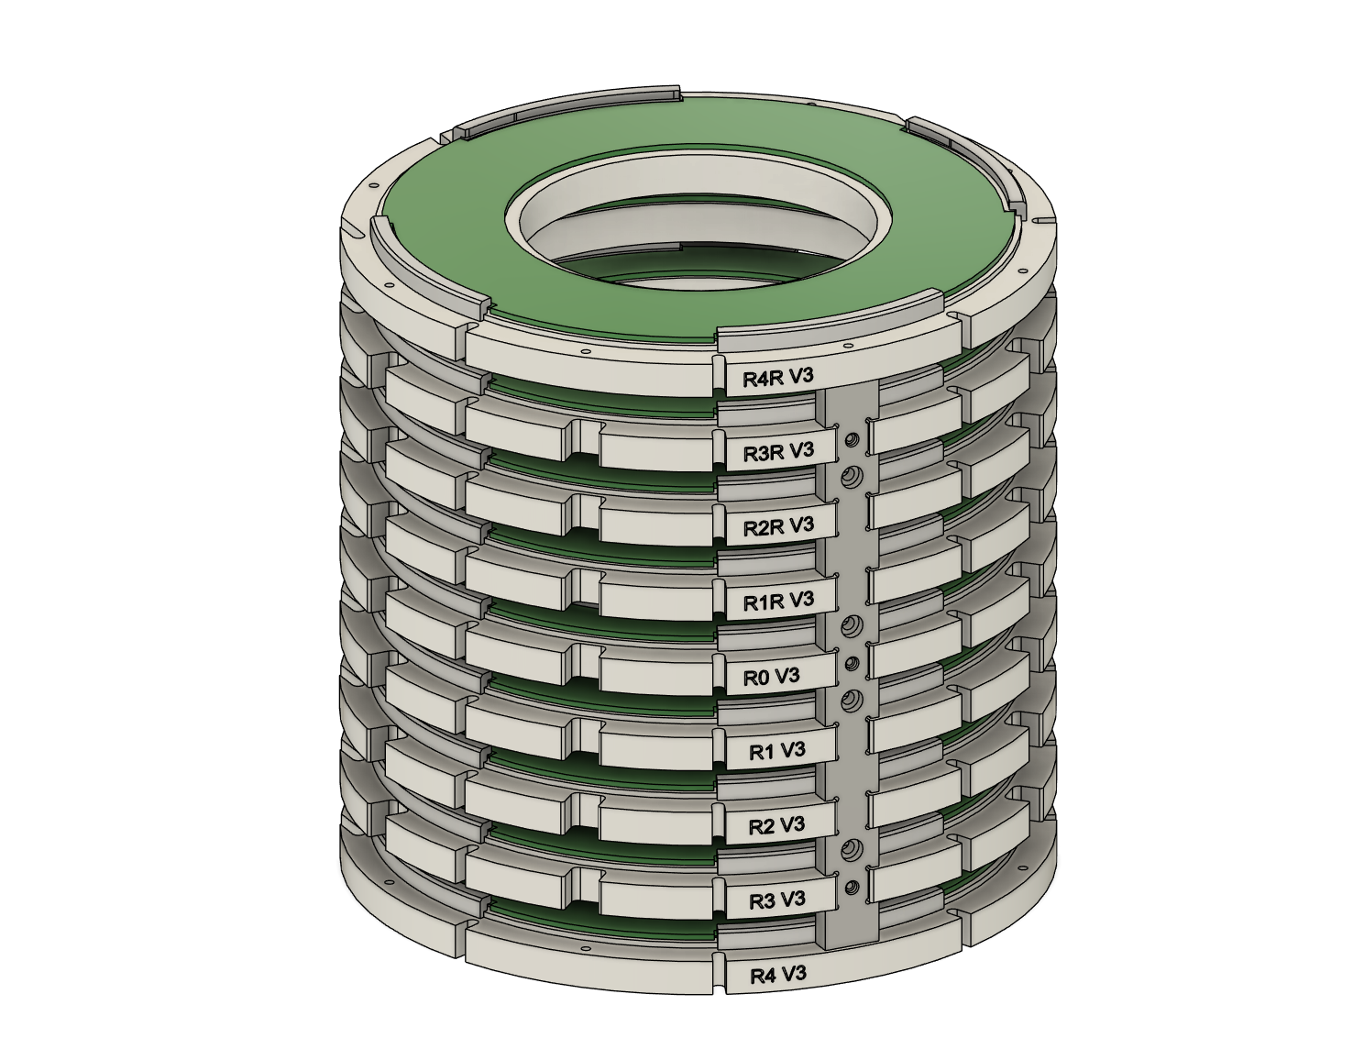
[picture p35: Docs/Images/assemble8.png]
image inserting R3 into locating bar
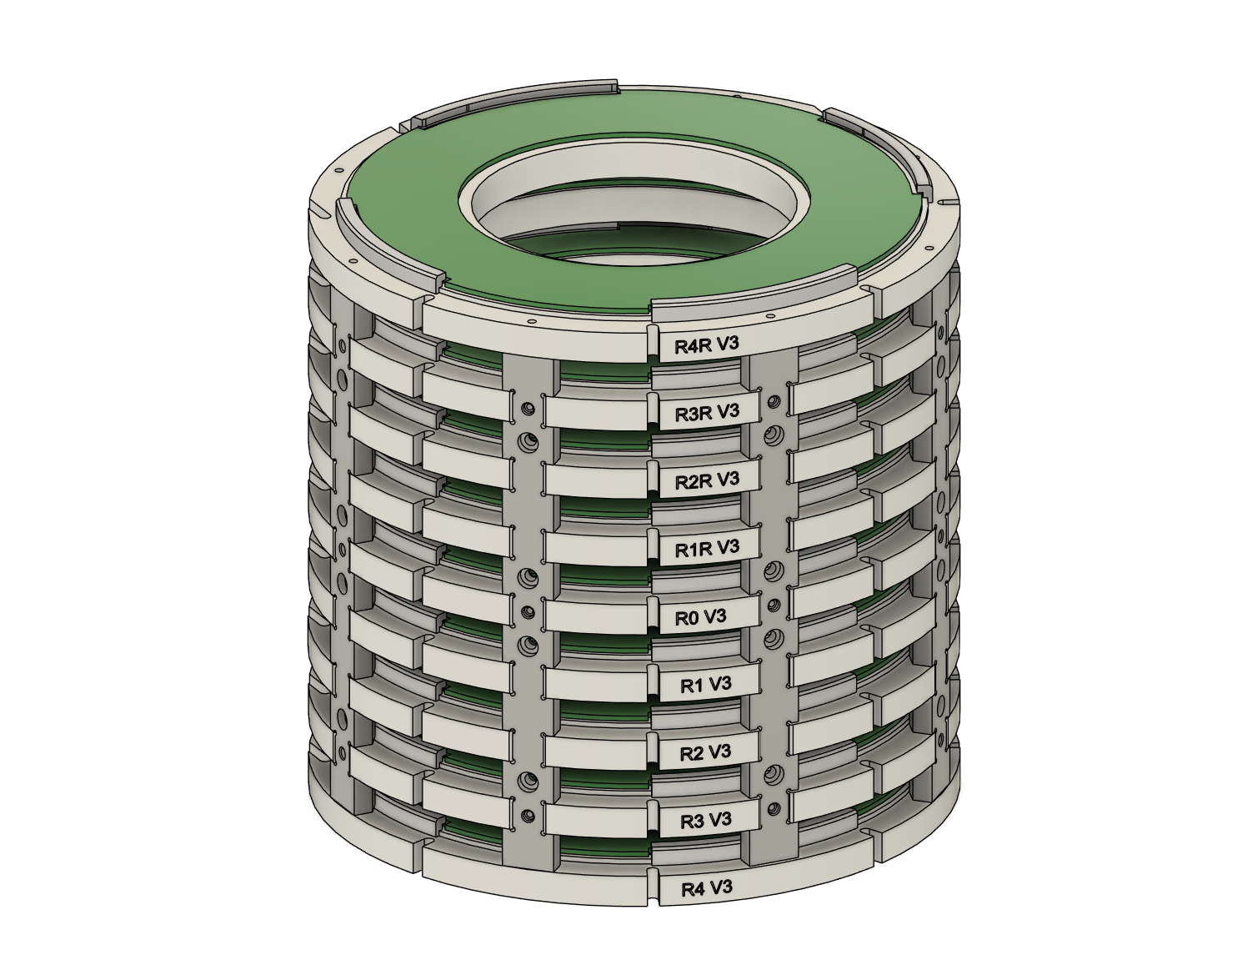
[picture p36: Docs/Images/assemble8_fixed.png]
image inserting R2 into locating bar
|||

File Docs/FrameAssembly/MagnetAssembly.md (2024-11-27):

# Inserting the Magets into the rings

Now that the necessary parts of the frame are printed, the insertion of the magnets into each ring can be done.

## Inserting the Magnets
Now that the holder and stamp are ready, let's start inserting the magnets into the rings. The process that was used may need improvement, but this was how they were mounted. The process is factory-like in nature and takes patience.

### Step 1: Test the Magnet
Take a single magnet and test it's $\vec{B}$- Field and polarity. Refer to the [Magnet Test Station](Docs/Tools/MagnetTestStation.md).

### Step 2: Insert the Magnet
Take your labeled magnet and align your marking to the notch of one of the holes in the ring.

| Magnet Housing Notch | Stamp in Use |
|:--:|:--:|
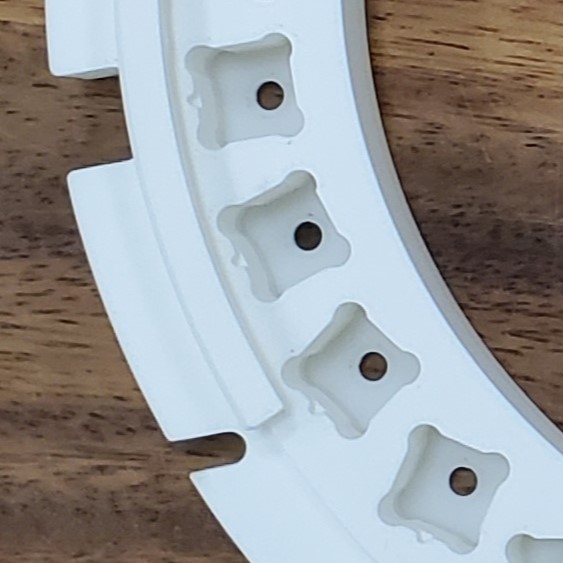
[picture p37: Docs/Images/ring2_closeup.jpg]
image of notch to align magnetic poles in the rings
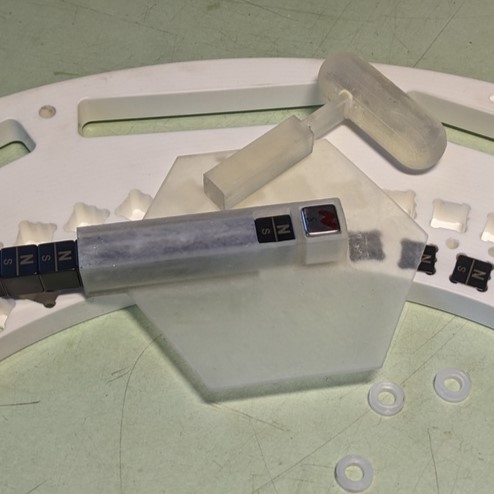
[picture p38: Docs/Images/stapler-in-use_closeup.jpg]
image of stamp in use
|||

### Step 3: Repeat
Repeat this process until an entire ring is completely filled in.

### Step 4: Secure the Ring
Once all the magnets are set in a single ring, secure the magnets with a plexi-glass lid

| Lid | Lid Inserted |
|:--:|:--:|
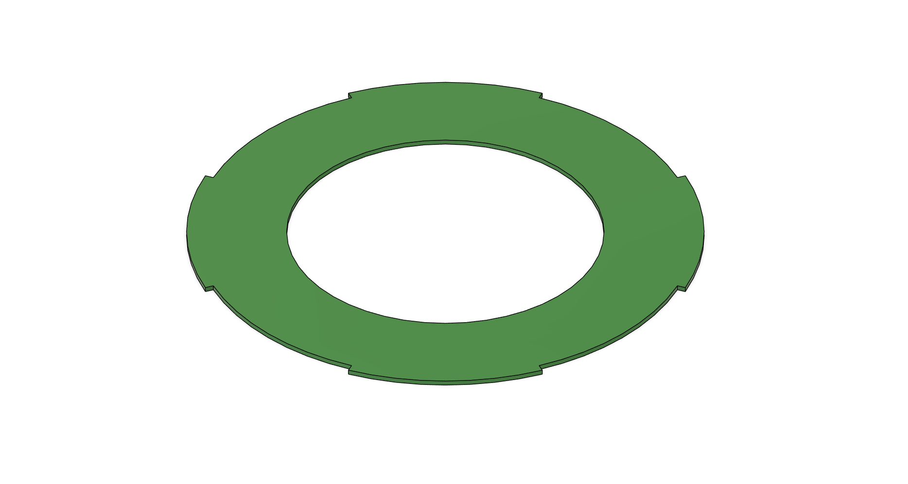
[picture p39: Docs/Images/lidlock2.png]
image of how the plexi-glass locks into the ring
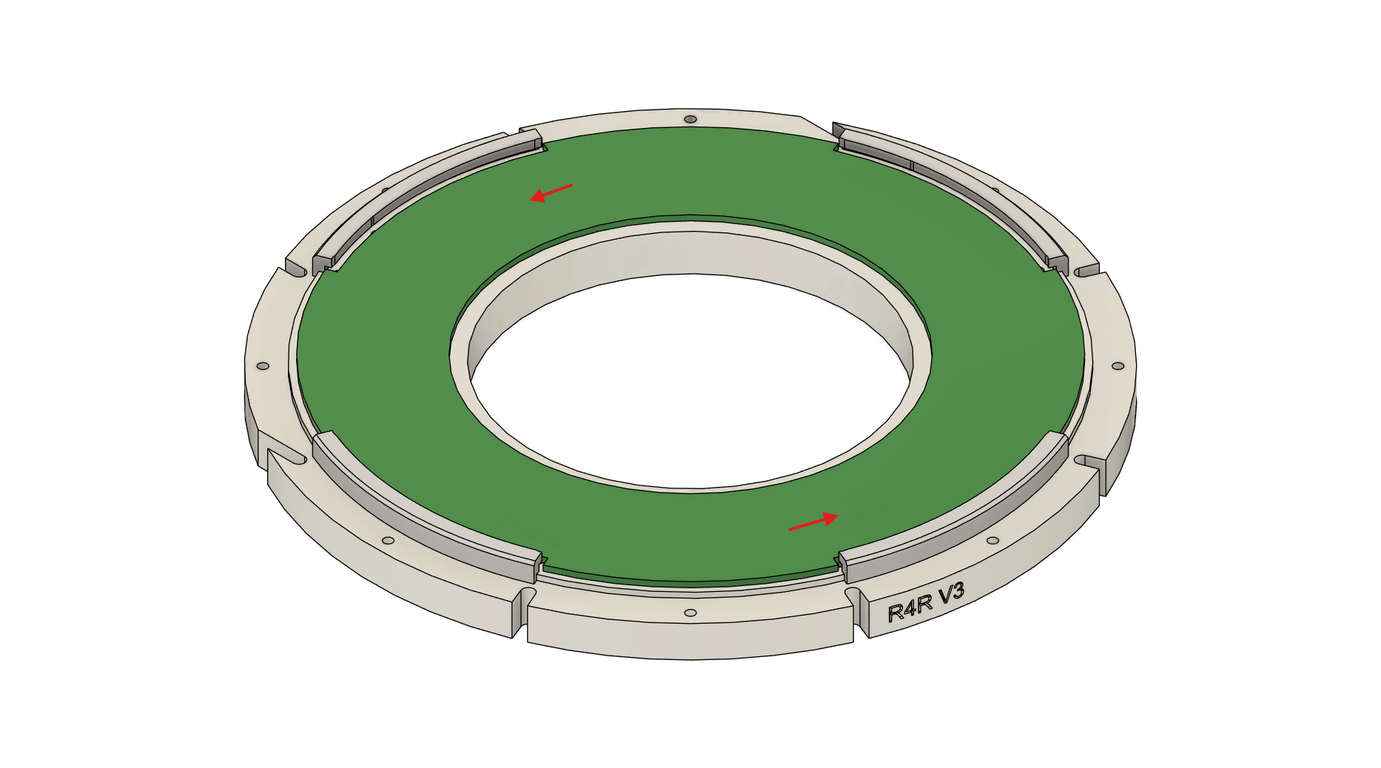
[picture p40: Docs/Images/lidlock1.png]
image of how the plexi-glass locks into the ring
|||

### Step 5: Repeat
Now repeat steps 1-4 until each ring is filled and secured.

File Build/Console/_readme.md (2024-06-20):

# OSII/Build/FieldScanner
Design files for converting a delta 3D printer to a 3D scanner for probing the magnetic field inside the Halbach magnet of the OSII Mini.

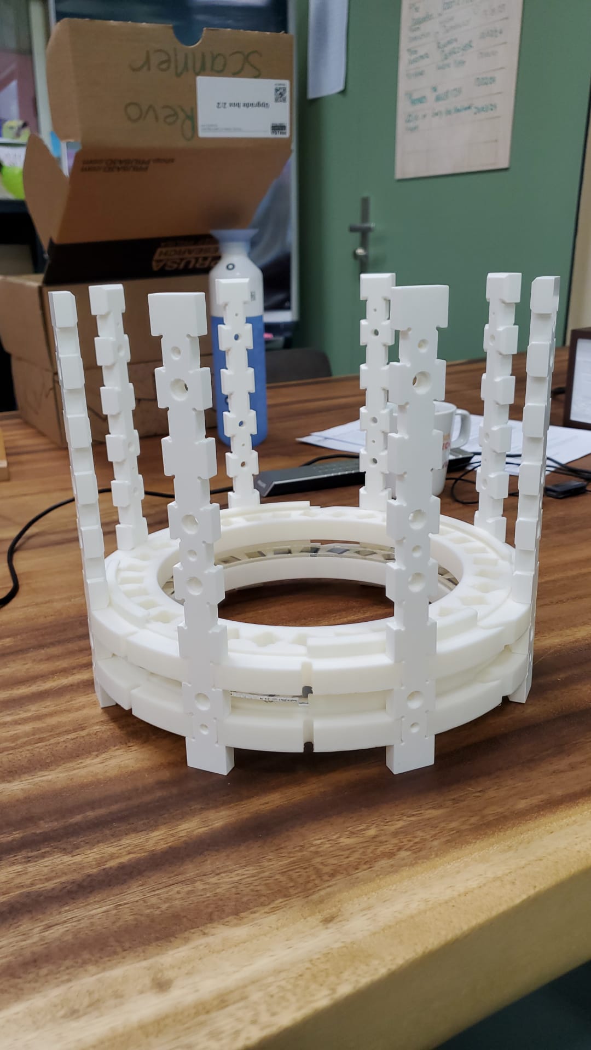
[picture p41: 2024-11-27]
Docs/Images/OSII_ONE_assembly.jpg

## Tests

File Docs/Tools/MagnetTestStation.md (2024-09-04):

# Magnet Test Station

This section outlines the process for testing the magnets that generate the main static field of the OSI<sup>2</sup> MINI. 

> [!NOTE]
> Please follow the [*Reference Magnet*](ReferenceMagnet.md) documentation before starting the magnet assembly.

## Magnetic Pole Identification
Once the reference magnet is established, the magnet test station will then utilize the known magnetic pole and $\vec{B}$- Field of the reference magnet to establish these same traits for the rest of the magnests of the system. This process should be done carefully and checked multiple times to ensure proper $\vec{B}$- Field alignment.

> [!CAUTION]
> Improper magnetic pole alignment and $\vec{B}$- Field strength can cause problems with $\vec{B}$- Field inhomogeneity and make imaging impossible for the MRI.

1. Separate one plane of the magnets from the batch of magnets. In the case of our current setup, the magnets had a divider in between planes.

  | Block of magnets | Modelled |
  | :---: | :--: |
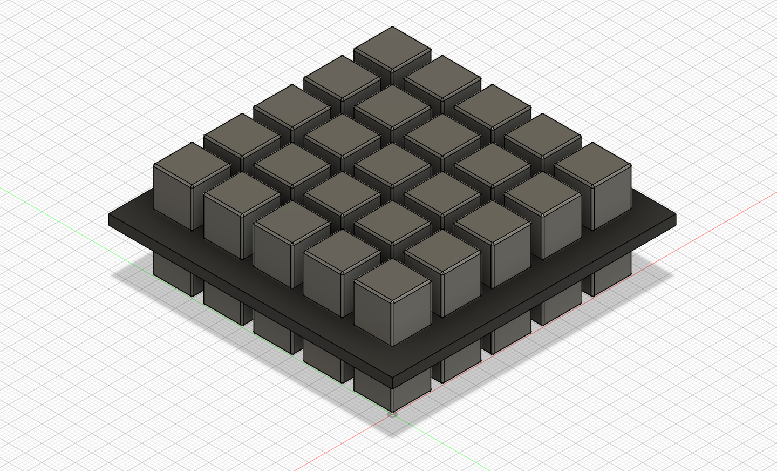
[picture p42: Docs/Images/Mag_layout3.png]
  |block of magnets| |

2. From the plane of magnets, form a single row. This technique aligns all of the poles of that row. I found that only doing one plane at a time minimizes the handling of the magnets, which reduces the potential of them attracting each other and breaking or chipping.

  | Row of magnets | Modelled |
  | :---: | :--: |
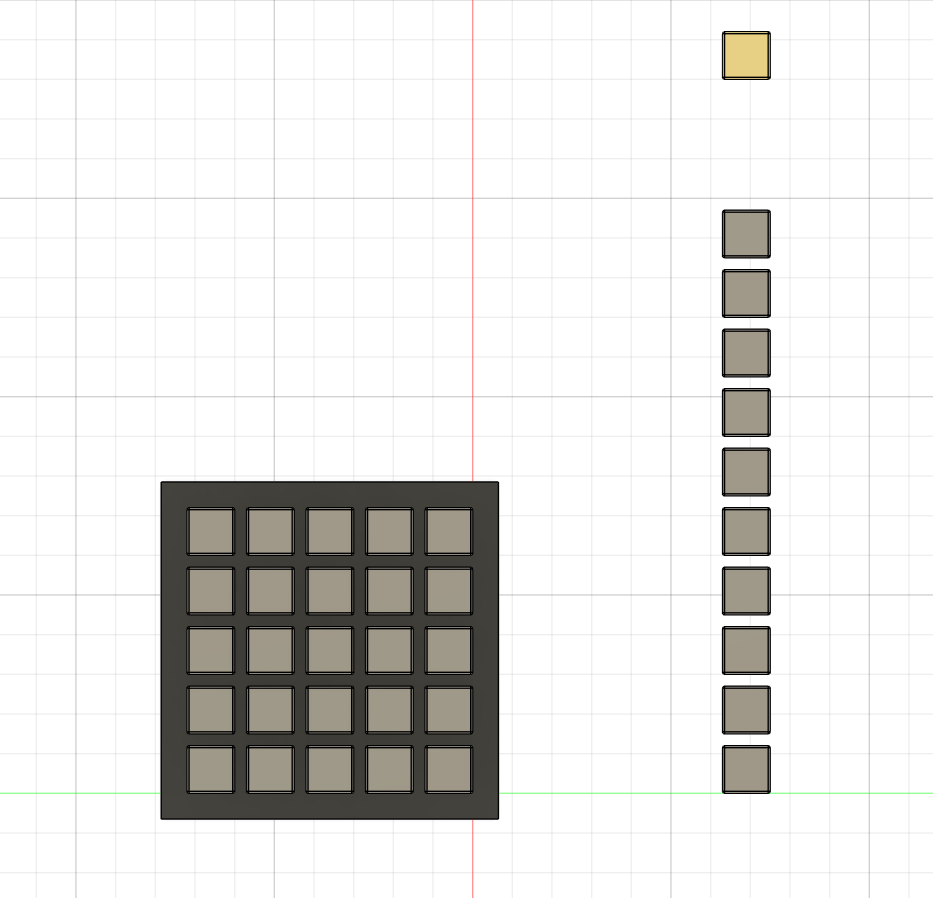
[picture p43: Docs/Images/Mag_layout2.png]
  |block of magnets| |

3. Next, pull one magnet from the row at a time. Set it into the [*Magnet Test Station*](../../Build/Tools/Frame-TestMagnetSupport.step) to double check pole orientation as well as ensuring that its $\vec{B}$- Field stregnth is within specification. In this setup, [*Spacer_A0*](../../Build/Tools/Spacer_A0-Spacer.step) or [*Spacer_A1*](../../Build/Tools/Spacer_A1-Spacer.step) is optimal for holding the 12mm magnets.

  | Spacer_A0 | Spacer_A1 | Magnet Test Station |
  | :---: | :--: |:--: |
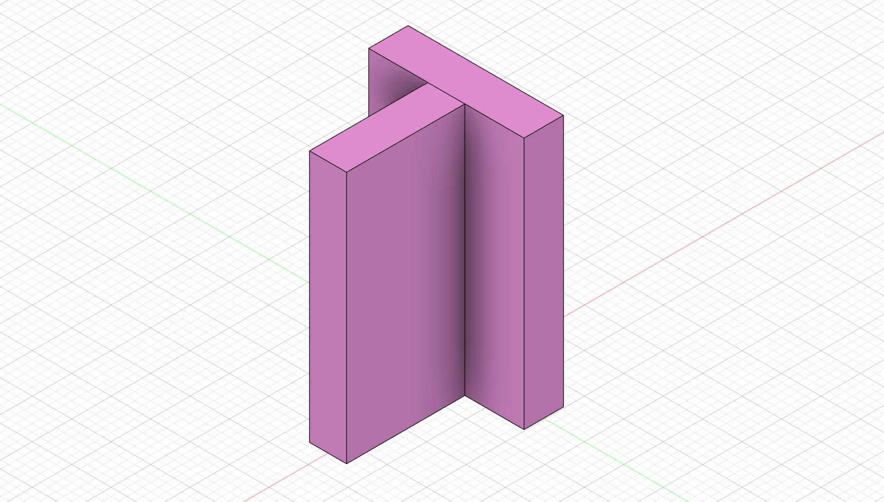
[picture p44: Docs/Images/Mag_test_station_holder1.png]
test station setup
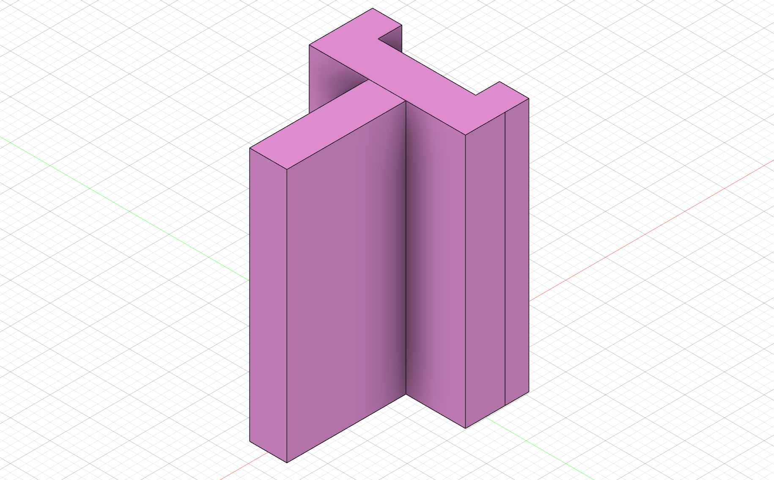
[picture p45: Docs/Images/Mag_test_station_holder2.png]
test station setup
  |||test station setup|

4. Once the Magnet Test Station is setup properly, connect the Arduino to your USB port. A detailed description and physical code can be found at the [*OSI<sup>2</sup> repository*](https://gitlab.com/osii/tools/MagnetTestStation). An example of what the interface looks like once you set it up is shown below.

  | Python Interface |
  | :---: |
  |python interface|

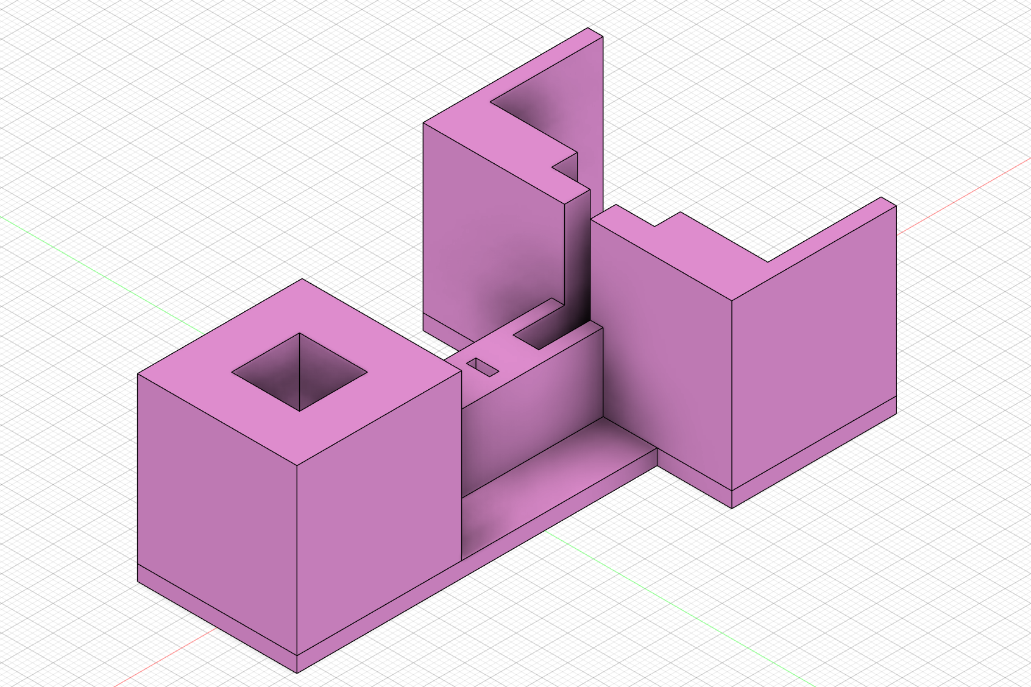
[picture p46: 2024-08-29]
Docs/Images/Mag_test_station.png

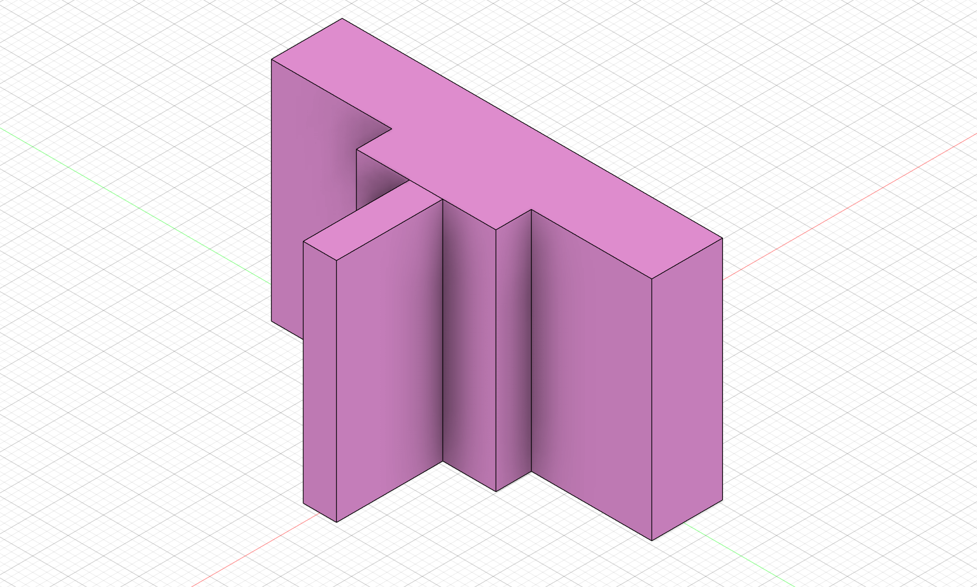
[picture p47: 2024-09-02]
Docs/Images/Mag_test_station_holder.png

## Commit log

2024-08-29 Hall Effect Sensor Diagrams
2024-09-02 CAD Files for magnet test station
    [Frame-TestMagnetSupport.step, Spacer_A0-Spacer.step, Spacer_A1-Spacer.step, Spacer_B0-Spacer.step]
2024-09-02 FreeCAD Files for magnet test station
    [Frame.FCStd, Spacer_A0.FCStd, Spacer_A1.FCStd, Spacer_B0.FCStd]
2024-09-02 Update and rename MagnetAssembly.md to MagnetTestStation.md
    I am going to separate the test station and mounting the magnets
2024-09-11 Hall Effect Sensor Datasheet
    Not the 3-axis but the one used for the reference magnet
2024-09-11 Update ReferenceMagnet.md
    added hall sensor datasheet link
2024-09-11 arduino and hall effect sensor schematic
2024-09-11 Update ReferenceMagnet.md
    Sensor wiring schematic upload
2024-09-11 python interface magnet calibration photos
2024-10-14 Update and rename Build/Tools/Frame-TestMagnetSupport.step to Build/Tools/step/Frame-TestMagnetSupport.step
    [Frame-TestMagnetSupport.step]
2024-10-14 Update and rename Build/Tools/Spacer_A0-Spacer.step to Build/Tools/step/Spacer_A0-Spacer.step
    [Spacer_A0-Spacer.step]
2024-10-14 Update and rename Build/Tools/Spacer_A1-Spacer.step to Build/Tools/step/Spacer_A1-Spacer.step
    [Spacer_A1-Spacer.step]
2024-10-14 Update and rename Build/Tools/Spacer_B0-Spacer.step to Build/Tools/step/Spacer_B0-Spacer.step
    [Spacer_B0-Spacer.step]
2024-10-14 added magnet test station arduino code
2024-10-29 Added initial version of shim optimization code
    [NIST_Smallbach_Swap_Smoothed_shell.csv, OSII_MINI.csv]
2024-10-31 Added fast shim optimization, helpers, and example data
    [NIST_Shim_ptp.csv, NIST_Smallbach_Swap_Smoothed.csv, OSII_MINI_reduced.csv]
2024-11-06 organising build files, adjusting readme
    [Frame-TestMagnetSupport.step, Frame.FCStd, Spacer_A0-Spacer.step, Spacer_A0.FCStd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]
2024-11-20 Changing location of Tool CAD files
    Will remove from CAD sub-folder
    [Frame-TestMagnetSupport.step, Frame.FCStd, Spacer_A0-Spacer.step, Spacer_A0.FCStd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]
2024-11-20 Delete Build/CAD directory
    Moved to sub-folder -> tools
    [Frame-TestMagnetSupport.step, Frame.FCStd, Spacer_A0-Spacer.step, Spacer_A0.FCStd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]
2024-11-20 Delete Docs/Magnets directory
    Changed to magnet assembly
2024-11-25 Upload Frame Fusion Files
    All versions and models
2024-11-25 Frame V3 Fusion File
2024-11-25 Delete Build/Frame/OSII_MINI_V3
    empty file
2024-11-25 Delete Build/Frame/OSII_Mini.zip
    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
2024-11-25 Magnet Lid files
    [Lid_A_V2 v2.dxf, Lid_A_V2 v2.f3z, Lid_A_V2 v2.step]
2024-11-25 Update and rename Build/Lid_A_V2 v2.dxf to Build/Magnet_Lid/Lid_A_V2 v2.dxf
    Created subfolder
    [Lid_A_V2 v2.dxf]
2024-11-25 Update and rename Build/Magnet_Lid/Lid_A_V2 v2.dxf to Build/Frame/Magnet_Lid/Lid_A_V2 v2.dxf
    created another subfolder
    [Lid_A_V2 v2.dxf]
2024-11-25 Rename Build/Lid_A_V2 v2.f3z to Build/Frame/Magnet_Lid/Lid_A_V2 v2.f3z
    [Lid_A_V2 v2.f3z]
2024-11-25 Update and rename Build/Lid_A_V2 v2.step to Build/Frame/Magnet_Lid/Lid_A_V2 v2.step
    [Lid_A_V2 v2.step]
2024-11-25 Update and rename Build/Lid_A_V2.svg to Build/Frame/Magnet_Lid/Lid_A_V2.svg
2024-11-25 Update and rename Build/Lid_A_V2_xtraclip.svg to Build/Frame/Magnet_Lid/Lid_A_V2_xtraclip.svg
2024-11-25 Update and rename Build/Lid_A_V2_xtraclipV2.svg to Build/Frame/Magnet_Lid/Lid_A_V2_xtraclipV2.svg
2024-11-25 Update and rename Build/Lid_A_V2_xtraclipV3.svg to Build/Frame/Magnet_Lid/Lid_A_V2_xtraclipV3.svg
2024-11-25 Update and rename Build/Lid_B_V2.svg to Build/Frame/Magnet_Lid/Lid_B_V2.svg
2024-11-25 Lid CAD Files
    [Lid_A_V2_xtraclip v3.dxf, Lid_A_V2_xtraclip v3.f3z, Lid_A_V2_xtraclip v3.step, Lid_B_V2 v3.dxf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]
2024-11-25 Ring 0 Fusion File
    [Ring_0_V3 v4.f3z]
2024-11-25 Rename Build/Frame/Ring_0_V3 v4.f3z to Build/Frame/Rings/Ring_0_V3 v4.f3z
    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
    [Ring_0_V3 v4.f3z]
2024-11-25 Rename Build/Frame/Rings/Ring_0_V3 v4.f3z to Build/Frame/Rings/Fusion_Files/Ring_0_V3 v4.f3z
    another subfolder
    [Ring_0_V3 v4.f3z]
2024-11-25 More Ring fusion files
    [Ring_1_V3 v1.f3z, Ring_1_V3_180 v5.f3z, Ring_2_V3 v4.f3z, Ring_2_V3_180 v2.f3z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]
2024-11-25 Ring dxf files
    [Ring_0_V3 v4.dxf]
2024-11-25 Rename Build/Frame/Rings/Ring_0_V3 v4.dxf to Build/Frame/Rings/DXF_Files/Ring_0_V3 v4.dxf
    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
    [Ring_0_V3 v4.dxf]
2024-11-25 More ring DXF files
    [Ring_1_V3 v1.dxf, Ring_1_V3_180 v5.dxf, Ring_2_V3 v4.dxf, Ring_2_V3_180 v2.dxf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]
2024-11-25 Overall OSII model and dependents
    [OSII Parameters v1.f3d]
2024-11-25 Misc Parts Files
    [Locating_bar v1.dxf]
2024-11-25 Update and rename Build/Frame/Locating_bar v1.dxf to Build/Frame/Locating_Bar/Locating_bar v1.dxf
    [Locating_bar v1.dxf]
2024-11-25 Update and rename Build/Frame/Magnet_Lid/Lid_A_V2 v2.dxf to Build/Frame/Magnet_Lid/DXF_Files/Lid_A_V2 v2.dxf
    [Lid_A_V2 v2.dxf]
2024-11-25 Rename Build/Frame/Magnet_Lid/Lid_A_V2 v2.f3z to Build/Frame/Magnet_Lid/Fusion_Files/Lid_A_V2 v2.f3z
    [Lid_A_V2 v2.f3z]
2024-11-25 Update and rename Build/Frame/Magnet_Lid/Lid_A_V2 v2.step to Build/Frame/Magnet_Lid/STEP/Lid_A_V2 v2.step
    [Lid_A_V2 v2.step]
2024-11-25 Update and rename Build/Frame/Magnet_Lid/Lid_A_V2.svg to Build/Frame/Magnet_Lid/SVG/Lid_A_V2.svg
2024-11-25 Update and rename Build/Frame/Magnet_Lid/Lid_A_V2_xtraclip v3.dxf to Build/Frame/Magnet_Lid/DXF_Files/Lid_A_V2_xtraclip v3.dxf
    [Lid_A_V2_xtraclip v3.dxf]
2024-11-25 Rename Build/Frame/Magnet_Lid/Lid_A_V2_xtraclip v3.f3z to Build/Frame/Magnet_Lid/Fusion_Files/Lid_A_V2_xtraclip v3.f3z
    [Lid_A_V2_xtraclip v3.f3z]
2024-11-25 Update and rename Build/Frame/Magnet_Lid/Lid_A_V2_xtraclip v3.step to Build/Frame/Magnet_Lid/STEP/Lid_A_V2_xtraclip v3.step
    [Lid_A_V2_xtraclip v3.step]
2024-11-25 Update and rename Build/Frame/Magnet_Lid/Lid_A_V2_xtraclip.svg to Build/Frame/Magnet_Lid/SVG/Lid_A_V2_xtraclip.svg
2024-11-25 Update and rename Build/Frame/Magnet_Lid/Lid_A_V2_xtraclipV2.svg to Build/Frame/Magnet_Lid/SVG/Lid_A_V2_xtraclipV2.svg
2024-11-25 Update and rename Build/Frame/Magnet_Lid/Lid_A_V2_xtraclipV3.svg to Build/Frame/Magnet_Lid/SVG/Lid_A_V2_xtraclipV3.svg
2024-11-25 Update and rename Build/Frame/Magnet_Lid/Lid_B_V2 v3.dxf to Build/Frame/Magnet_Lid/DXF_Files/Lid_B_V2 v3.dxf
    [Lid_B_V2 v3.dxf]
2024-11-25 Rename Build/Frame/Magnet_Lid/Lid_B_V2 v3.f3z to Build/Frame/Magnet_Lid/Fusion_Files/Lid_B_V2 v3.f3z
    [Lid_B_V2 v3.f3z]
2024-11-25 Update and rename Build/Frame/Magnet_Lid/Lid_B_V2 v3.step to Build/Frame/Magnet_Lid/STEP/Lid_B_V2 v3.step
    [Lid_B_V2 v3.step]
2024-11-25 Update and rename Build/Frame/Magnet_Lid/Lid_B_V2.svg to Build/Frame/Magnet_Lid/SVG/Lid_B_V2.svg
2024-11-25 Misc Parts
    [M4_threaded_brass v1.dxf]
2024-11-25 Update and rename Build/Frame/M4_threaded_brass v1.dxf to Build/Frame/Hardware/M4_threaded_brass v1.dxf
    [M4_threaded_brass v1.dxf]
2024-11-25 More hardware
    [93187A150_NO THREADS_Brass Thin Hex Nut v1.dxf, 93187A150_NO THREADS_Brass Thin Hex Nut v1.f3d, 94500A283_NO THREADS_316 Stainless Steel Button Head Hex Drive 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]
2024-11-25 Fixed the Fusion File of the overall frame
2024-11-25 Update PrintRings.md
    Filling out how to print the mri rings
2024-11-25 Update PrintRings.md
    First draft of how to print rings
2024-11-25 Update and rename PrintRings.md to PrintFrame.md
    changed name so to include the locating bar printing process
2024-11-25 Update PrintFrame.md
    Added locating bar information
2024-11-25 Update PrintFrame.md
    Added link to find locating bar files
2024-11-25 Magnet holder files
    [clamp-Body.step, clamp.FCStd, holder-Body.step, holder.FCStd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]
2024-11-25 Stamp mod files
    [holder-Body v2.dxf, holder-Body v2.f3d]
2024-11-25 Rename holder-Body v2.f3d to holder-modv2.f3d
    [holder-modv2.f3d]
2024-11-25 Update and rename holder-Body v2.dxf to holder_modv2.dxf
    [holder_modv2.dxf]
2024-11-27 Update FrameAssembly.md
    first lines of how to assemble the frame
2024-11-27 osii mini assembly
2024-11-27 frame images
2024-11-27 assembly process images
2024-11-27 assembly8 image
2024-11-27 assembly 8 fixed
2024-11-27 Update FrameAssembly.md
    Finished step where mounting endcap rings
2024-12-09 organizing the assembly steps and folders
    [93187A150_NO THREADS_Brass Thin Hex Nut v1.dxf, 93187A150_NO THREADS_Brass Thin Hex Nut v1.f3d, 94500A283_NO THREADS_316 Stainless Steel Button Head Hex Drive 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]
2025-01-30 fieldscanner documentation
    [3D-attachment.FCStd]
